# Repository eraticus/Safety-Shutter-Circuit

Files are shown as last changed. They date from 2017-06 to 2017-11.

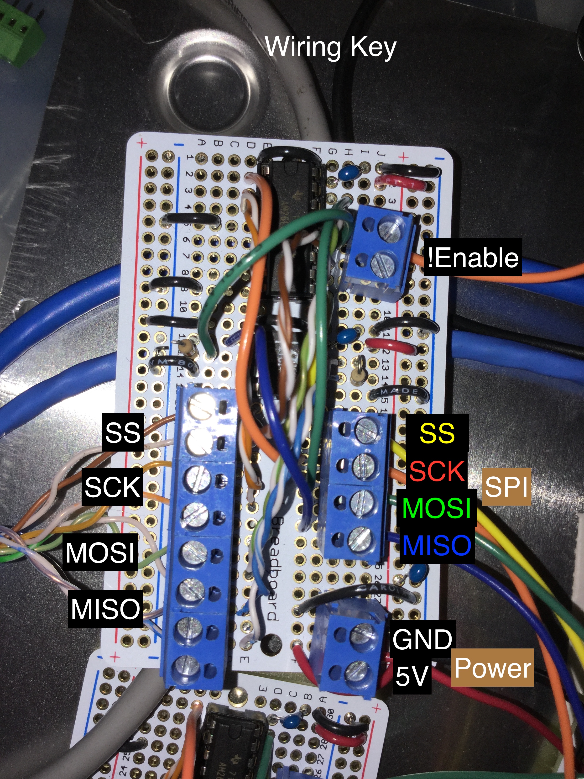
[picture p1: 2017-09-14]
images/IMG_2744.JPG

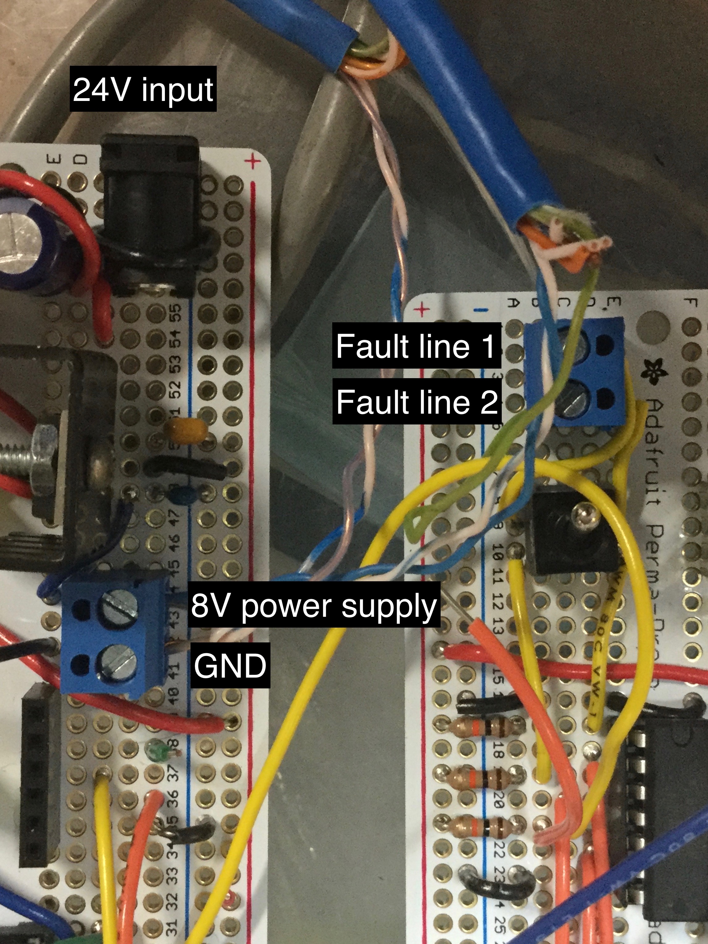
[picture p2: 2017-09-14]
images/IMG_2812.jpg

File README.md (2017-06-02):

# Safety-Shutter-Circuit
Circuit to close shutter if light levels get too high.
The project is separated into three components:
a) Sensors: photodiode amplifier circuit with comparator. Comparator goes low if light too high.
b) ADC: Can be connected with up to four sensor boards. ADC converts light level to digital value. Communication with Shutter Control board via SPI over differential pairs. Also, sensor comparator values ANDed. If a sensors comparator goes low, then a separate low signal sent to shutter control.
c) Shutter Control: Shutter control has multiple subsystems
  1) If a low signal is received from the ADC, a latch is set which controls the state of the shutter.
  2) The light levels are monitored, via the ADC boards, and if the light level approaches the threshold, the shutter is closed.
  3) Communication to LANTRONIX via RS-232 driver connected to RX/TX of microcontroller.

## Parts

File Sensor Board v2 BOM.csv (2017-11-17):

Digi-Key Part Number | Manufacturer | Manufacturer Part Number | Customer Reference | Quantity 1 | Quantity 2 | Quantity 3 | Mfg Std Lead Time | Description | Comments | RoHS Status | Lead Free Status | REACH Status
36-5015CT-ND | KEYSTONE ELECTRONICS (VA) | 5015 | TEST POINTS FOR FIELD CALIBRATION | 5 | 0 | 0 | 4 Weeks | PC TEST POINT MINIATURE SMT |  | RoHS Compliant | Lead free | Unaffected Jan-2017
399-1284-1-ND | KEMET (VA) | C0805C105K4RACTU | DECOUPLING CAPS FOR REGULATOR, ETC | 5 | 0 | 0 | 23 Weeks | CAP CER 1UF 16V X7R 0805 |  | RoHS Compliant | Lead free | Unaffected Jan-2017
3224G-1-103ECT-ND | BOURNS INC (VA) | 3224G-1-103E | FOR SETTING THRESHOLD VALUE | 1 | 0 | 0 | 8 Weeks | TRIMMER 10K OHM 0.25W SMD |  | RoHS Compliant | Lead free | Unaffected Jan-2017
160-1032-ND | LITE-ON INC | LTR-516AD | PHOTODIODE WITH DAYLIGHT FILTER | 1 | 0 | 0 | 14 Weeks | PHOTODIODE IR DARK |  | RoHS Compliant | Lead free | Not Available
MCP6541T-E/OTCT-ND | MICROCHIP TECHNOLOGY (VA) | MCP6541T-E/OT | SETS FAULT LINE BY COMPARING SENSOR TO THRESHOLD | 1 | 0 | 0 | 8 Weeks | IC COMP 1.6V SNGL P-P SOT23-5 |  | RoHS Compliant | Lead free | Unaffected Jan-2017
MCP6001T-E/OTCT-ND | MICROCHIP TECHNOLOGY (VA) | MCP6001T-E/OT | CHANGE PHOTOCURRENT TO VOLTAGE SIGNAL | 1 | 0 | 0 | 4 Weeks | IC OPAMP GP 1MHZ RRO SOT23-5 |  | RoHS Compliant | Lead free | Unaffected Jan-2017
MCP1702T-5002E/CBCT-ND | MICROCHIP TECHNOLOGY (VA) | MCP1702T-5002E/CB | 5 VOLT REG. USED TO POWER BOARD | 1 | 0 | 0 | 5 Weeks | IC REG LINEAR 5V 250MA SOT23A-3 |  | RoHS Compliant | Lead free | Unaffected Jan-2017
ED10564-ND | ON SHORE TECHNOLOGY INC | OSTVN05A150 | POWER INPUT SIGNAL OUTPUT | 1 | 0 | 0 | 10 Weeks | CONN TERM BLOCK 2.54MM 5POS PCB |  | RoHS Compliant | Lead free | Unaffected Jul-2017
399-1113-1-ND | KEMET (VA) | C0805C220J5GACTU | FEEDBACK STABILIZATION CAP | 1 | 0 | 0 | 18 Weeks | CAP CER 22PF 50V C0G/NP0 0805 |  | RoHS Compliant | Lead free | Unaffected Jan-2017
399-7442-1-ND | KEMET (VA) | C1206C106K3RACTU | UNREGULATED POWER INPUT CAP | 1 | 0 | 0 | 27 Weeks | CAP CER 10UF 25V X7R 1206 |  | RoHS Compliant | Lead free | Unaffected Jan-2017
YAG1242CT-ND | YAGEO (VA) | RT1206FRE0710KL | FEEDBACK RESISTOR | 1 | 0 | 0 | 20 Weeks | RES SMD 10K OHM 1% 1/4W 1206 | Alternate Packaging Exists | RoHS Compliant | Lead free | Unaffected Jul-2017

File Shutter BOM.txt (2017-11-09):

Partlist exported from /Users/eraticus/Library/Mobile Documents/com~apple~CloudDocs/Safety-Shutter-Circuit/Shutter.sch at 11/8/17 4:27 PM

Part                     Value                     Device                             Package                 Description                                   MF MPN         OC_FARNELL OC_NEWARK PROD_ID   
ADC1                     M08                       M08                                OSTVN08                                                                                                             
ADC1_FAULT               M03                       M03                                OSTVN03                                                                                                             
ADC2                     M08                       M08                                OSTVN08                                                                                                             
ADC2_FAULT               M03                       M03                                OSTVN03                                                                                                             
BUFFER_OD1:04CAP         100n                      CAP805B                            0805_B                                                                                                              
BUFFER_OD1:IC6           74AC04D                   74AC04D                            SO14                    Hex INVERTER                                                                                
BUFFER_OD1:IC7           74ALS05D                  74ALS05D                           SO14                    Hex INVERTER, open collector                                                                
BUFFER_OD1:O5CAP         100n                      CAP805B                            0805_B                                                                                                              
C1                       1u                        CAP5MM                             CAP_CER_TDK_FK28_5MM    Ceramic Capacitor                                                                           
C2                       1u                        CAP5MM                             CAP_CER_TDK_FK28_5MM    Ceramic Capacitor                                                                           
C3                       1u                        CAP5MM                             CAP_CER_TDK_FK28_5MM    Ceramic Capacitor                                                                           
C4                       1u                        CAP5MM                             CAP_CER_TDK_FK28_5MM    Ceramic Capacitor                                                                           
C5                       100n                      CAP805B                            0805_B                                                                                                              
C6                       100n                      CAP805B                            0805_B                                                                                                              
C7                       100n                      CAP805B                            0805_B                                                                                                              
C8                       100n                      CAP805B                            0805_B                                                                                                              
C9                       100n                      CAP805B                            0805_B                                                                                                              
C10                      100n                      CAP805B                            0805_B                                                                                                              
C11                      100n                      CAP805B                            0805_B                                                                                                              
C12                      100n                      CAP805B                            0805_B                                                                                                              
C13                      100n                      CAP805B                            0805_B                                                                                                              
C14                      100n                      CAP805B                            0805_B                                                                                                              
C15                      100n                      CAP805B                            0805_B                                                                                                              
C16                      1u                        CAP5MM                             CAP_CER_TDK_FK28_5MM    Ceramic Capacitor                                                                           
C17                      10u                       CAP_POL8_3.5                       CAP_POL_8_3.5           Polarized Capacitor, such as Electrolytic                                                   
C18                      1u                        CAP5MM                             CAP_CER_TDK_FK28_5MM    Ceramic Capacitor                                                                           
C19                      100n                      CAP805B                            0805_B                                                                                                              
CO[                      100n                      CAP805B                            0805_B                                                                                                              
D1                       AM26C31                   AM26C31                            SOIC_16_NARROW          Quadruple Differential Line Driver                                                          
D2                       AM26C31                   AM26C31                            SOIC_16_NARROW          Quadruple Differential Line Driver                                                          
D3                       1N4004                    1N4004                             DO41-10                 DIODE                                                                                       
DEWAR_SWITCH             M02                       M02                                OSTVN02                                                                                                             
IC3                      MAX3222                   MAX3222                            DIL18                   RS232 TRANSCEIVER                                MAX3222EPN+ 1188044    99K3237             
IC4                      74AC00D                   74AC00D                            SO14                    Quad 2-input NAND gate                                                                      
J1                       ATMEL_PROGRAMMER_HEADERTH ATMEL_PROGRAMMER_HEADERTH          ATMEL_PROGRAMMER_HEADER Board connector for Atmel MkII ISP programmer                                               
J2                                                 M06NO_SILK_FEMALE_PTH              1X06_NO_SILK            Header 6                                                                          CONN-08437
MC7808                   7808T                     7808T                              TO220H                  Positive VOLTAGE REGULATOR                                                                  
MC7812                   7812TV                    7812TV                             TO220V                  Positive VOLTAGE REGULATOR                                                                  
OPEN_CLOSE_TOGGLE        M03                       M03                                OSTVN03                                                                                                             
POWER                    M02                       M02                                OSTVN02                                                                                                             
R1                       10K                       RESISTOR0805                       0805                                                                                                                
R2                       100                       RESISTOR0805                       0805                                                                                                                
R3                       100                       RESISTOR0805                       0805                                                                                                                
R4                       10K                       RESISTOR0805                       0805                                                                                                                
R5                       10K                       RESISTOR0805                       0805                                                                                                                
R6                       10K                       RESISTOR0805                       0805                                                                                                                
R7                       10K                       RESISTOR0805                       0805                                                                                                                
R8                       1.6K                      RESISTOR0805                       0805                                                                                                                
SHUTTER                  M02                       M02                                OSTVN02                                                                                                             
SHUTTER_CLOSED_INDICATOR M02                       M02                                OSTVN02                                                                                                             
SHUTTER_OPEN_INDICATOR   M02                       M02                                OSTVN02                                                                                                             
SHUTTER_SWITCH           M02                       M02                                OSTVN02                                                                                                             
T1                       TIP131                    TIP131                             TO220                   NPN BIPOLAR DARLINGTON TRANSISTOR                                                           
U$1                      ATMEGA_32828PDIP          ATMEGA_32828PDIP                   DIP-28                                                                                                              
U$2                      RESONATOR                 RESONATOR                          CSTCE                                                                                                               
U$3                      TACTILE                   TACTILE                            CB315FP                                                                                                             
U$4                      MO3                       MO3                                OSTVN03                                                                                                             
U$5                      LTC1485DIP                LTC1485DIP                         DIP-8                                                                                                               
U$6                      LTC1485DIP                LTC1485DIP                         DIP-8                                                                                                               
U$7                      DPDTA_DP                  DPDTA_DP                           A_DP_STRAIGHT_BRACKET                                                                                               
U1                                                 VOLTAGE_REGULATOR_LDOMCP1702_TO-92 TO-92                   MCP1702 3 terminal LDO                                                                      
V1                       POWER_JACK                POWER_JACK                         PJ-102AH                Standard Power Jack with Switch

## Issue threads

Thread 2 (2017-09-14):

### ISSUE TITLE
Create and test chopper amp noninverting circuit

### ISSUE THREAD

**Issue by meyerjohn** [eraticus/Safety-Shutter-Circuit#2]
Verify that basic noninverting op amp circuit will give zero (or near zero) output for V(inverting) == V(noninverting) == GND. Test this for high gains or high resistor values.

This is to test idea for suitability for second stage voltage amplifier circuit, if voltages from transimpedance stage are not high enough for ADC

**Comment by eraticus** [comment]
This might be a good idea to test. However, since we are not using a far IR diode, I'm going to close this for now. It would be a good idea to test a chopper amp within the current circuit architecture.

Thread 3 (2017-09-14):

### ISSUE TITLE
Find appropriate ADC with interrupt pin

### ISSUE THREAD

**Issue by meyerjohn** [eraticus/Safety-Shutter-Circuit#3]
It would be convenient to shutdown the microcontroller and communications while an ADC event is occurring so that switching noise does not affect the process.

The idea here is to initiate the ADC process, then sleep the controller. The controller when wakes when the ADC is finished and indicated by an interrupt pin. The controller can then read and communicate the values.

I believe that MAXIM has ADCs that operate at 5V, and have interrupt pins to indicate that a conversion is ready to read in.

**Comment by eraticus** [comment]
I did not find an ADC with an interrupt. So I designed the circuit with the MCP3008 10bit ADC.

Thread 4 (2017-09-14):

### ISSUE TITLE
Find values for photodiode

### ISSUE THREAD

**Issue by meyerjohn** [eraticus/Safety-Shutter-Circuit#4]
When Jaren did his Akamai project, he had expected current values that I would like to use in calculating op amp circuit gains. I also need to know what the capacitance of the photodiode is, in order to calculate stability, and capacitor compensation values.

This should be in my old notebook. If not, contact Jaren and Andre.

**Comment by eraticus** [comment]
Not using the far IR photodiodes. I use commercial 940nm photodiodes instead, since they will be mounted outside the dewar

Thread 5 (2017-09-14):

### ISSUE TITLE
Design NAND SR-Latch with avoidance of forbiden 00 state

### ISSUE THREAD

**Issue by meyerjohn** [eraticus/Safety-Shutter-Circuit#5]
I want to avoid both inputs going low, which would occur if there was an attempt to reset the latch when the circuit is currently faulting.

I have an idea of gating the input to S via an AND gate. By tying input A of the AND to R, the value of AND becomes a buffer for the B input. Attaching Y of AND to a 74HC05 makes it a NAND with OC output.

A 74HC03 chip is not a normally stocked part, but it is available.

**Comment by eraticus** [comment]
I'm closing this without rewiring the circuit for LOW/LOW input avoidance. This is because I don't anticipate this to be a problem. The interface via micro controller can check the state of the photodiodes first (via the fault lines).

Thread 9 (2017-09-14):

### ISSUE TITLE
Install MCP3008 10 bit ADC

### ISSUE THREAD

**Issue by meyerjohn** [eraticus/Safety-Shutter-Circuit#9]
Maybe don't write separate library, but have all code that interfaces with MCP3008 in a separate file.
[datasheet](http://ww1.microchip.com/downloads/en/DeviceDoc/21295d.pdf)

**Comment by eraticus** [comment]
The code for the MCP3008 is complete. There are some "improvements" that could be done, such as separating into a lib, and left justifying the data, and only using 8bits. I will wait for someone to ask me for this though. It works now.

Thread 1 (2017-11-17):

### ISSUE TITLE
Documentation: Create spreadsheet for stability and gain calculations for candidate op amps

### ISSUE THREAD

**Issue by meyerjohn** [eraticus/Safety-Shutter-Circuit#1]
Need this to determine applicability of a particular op amp, and maximum gain. Maximum gain might be limited by maximum resistor value is available.

**Comment by eraticus** [comment]
I did these calculations earlier for the feedback capacitor on the transconductive op amp circuits for the photodiode. Not sure if I need to preserve, but find the white paper that the work was based on for reference. I think it was a Microchip white paper

**Comment by eraticus** [comment]
Since the gain resistor has been reduced to 10K, this is no longer really necessary.

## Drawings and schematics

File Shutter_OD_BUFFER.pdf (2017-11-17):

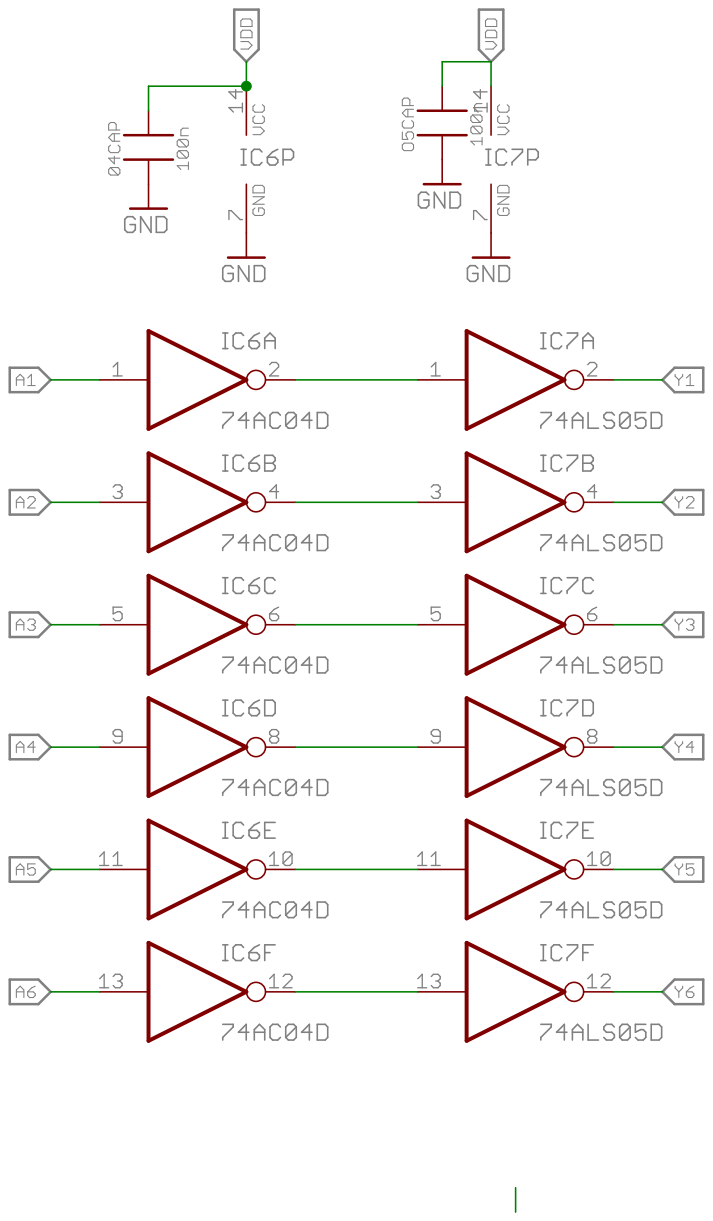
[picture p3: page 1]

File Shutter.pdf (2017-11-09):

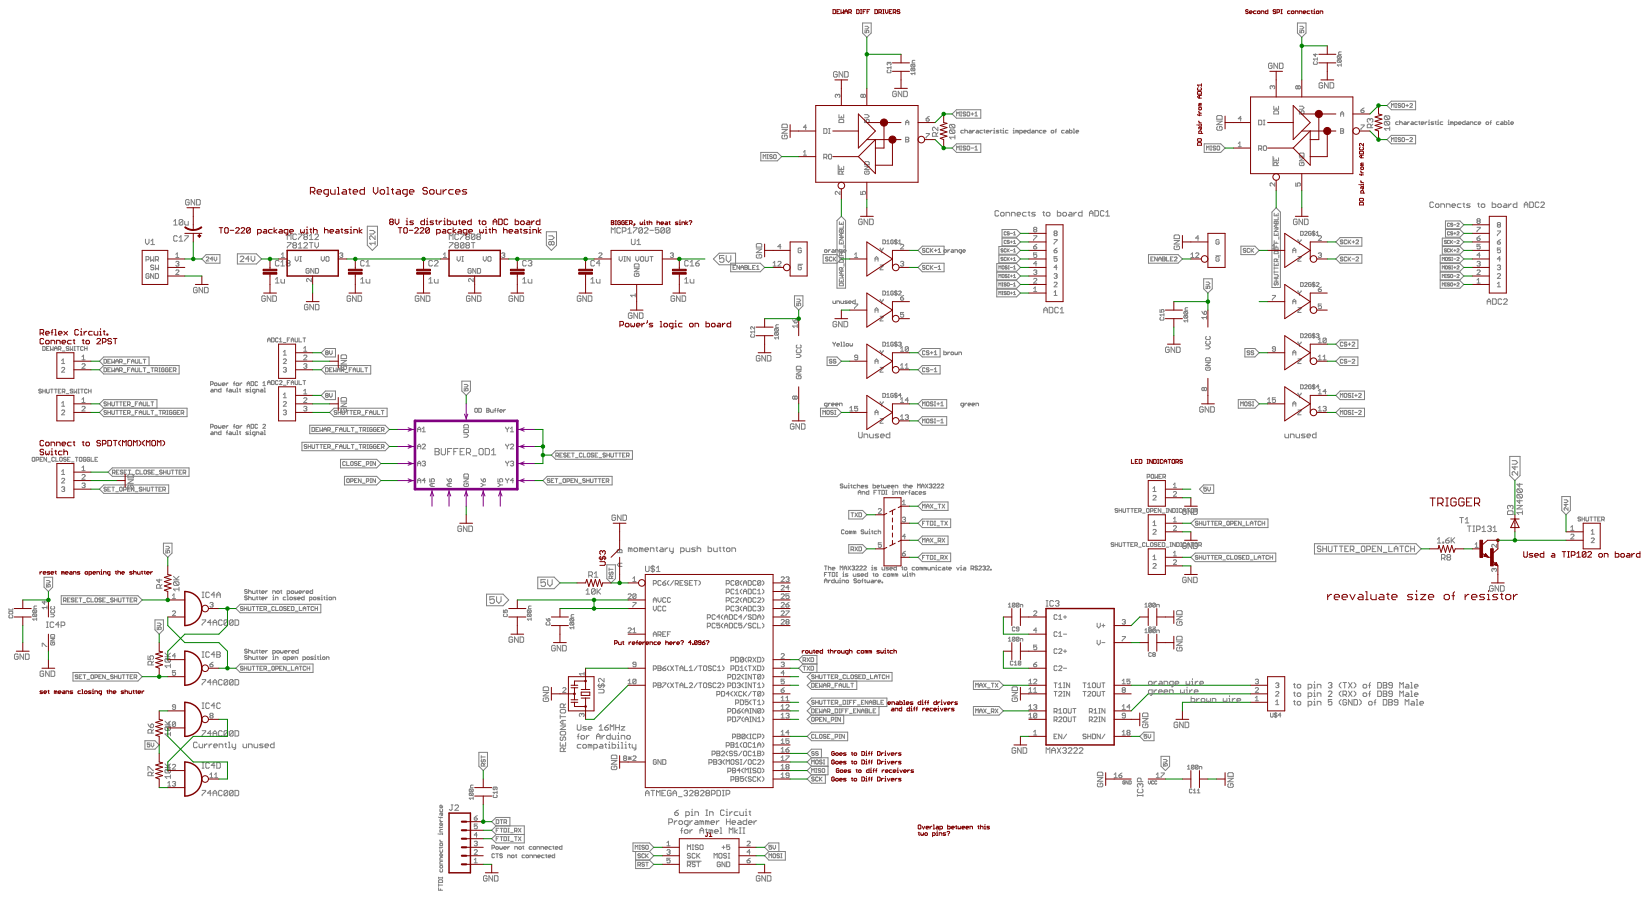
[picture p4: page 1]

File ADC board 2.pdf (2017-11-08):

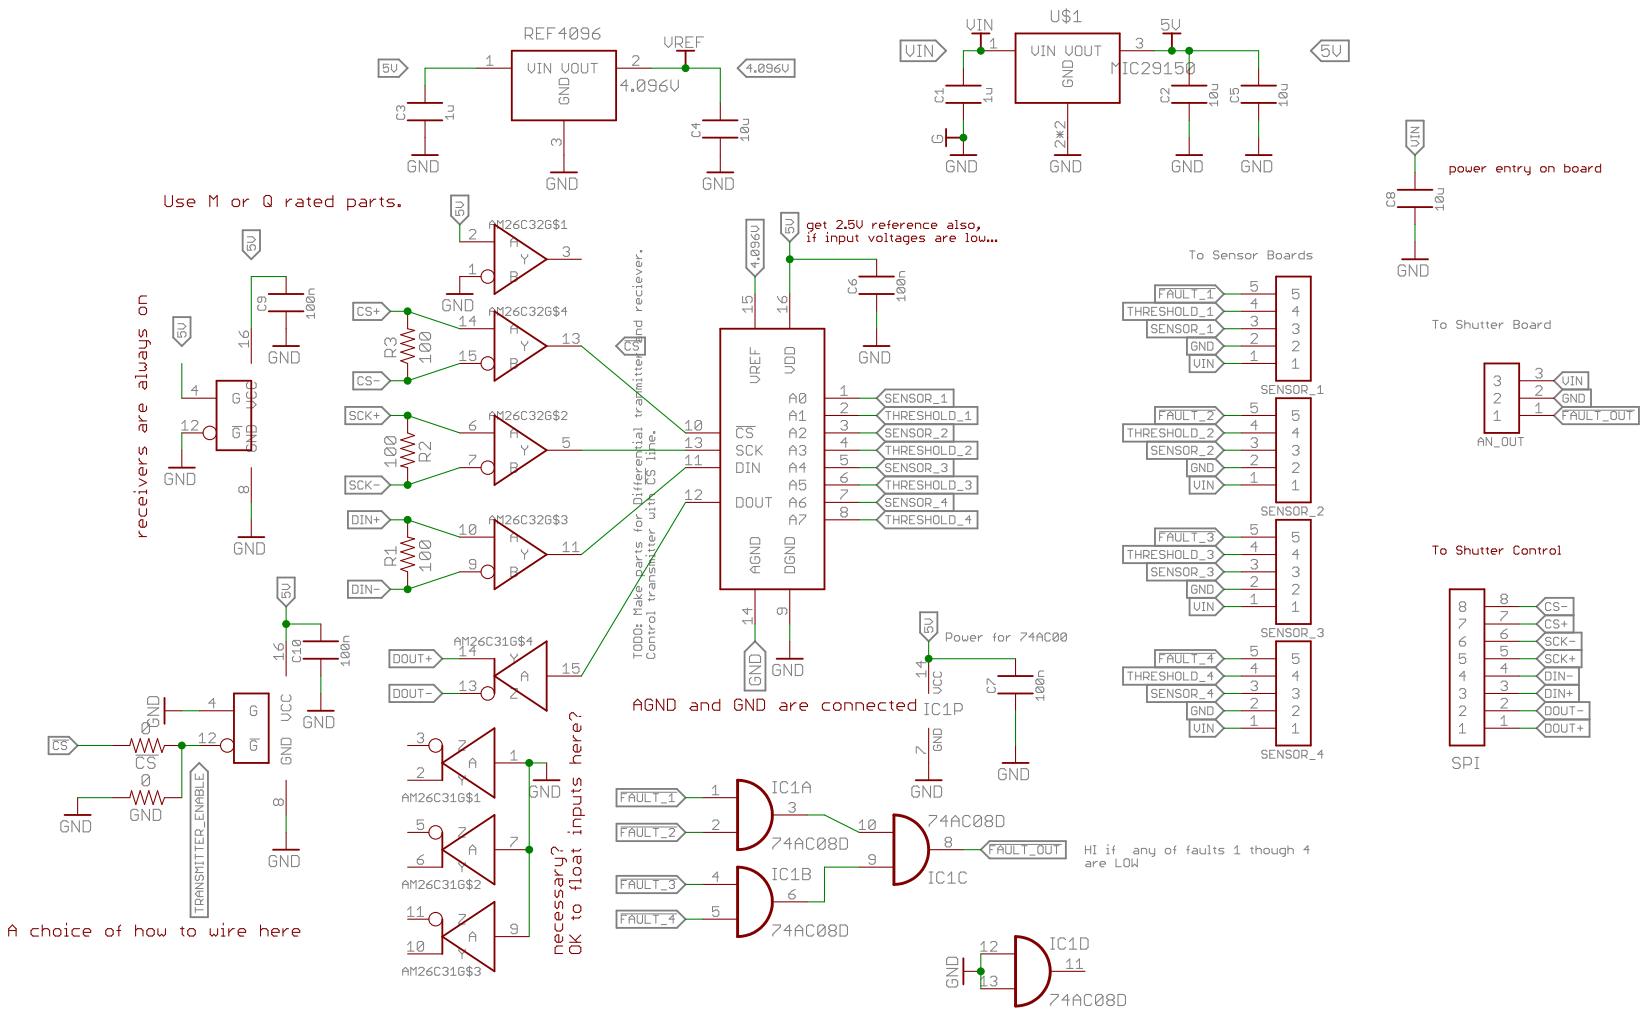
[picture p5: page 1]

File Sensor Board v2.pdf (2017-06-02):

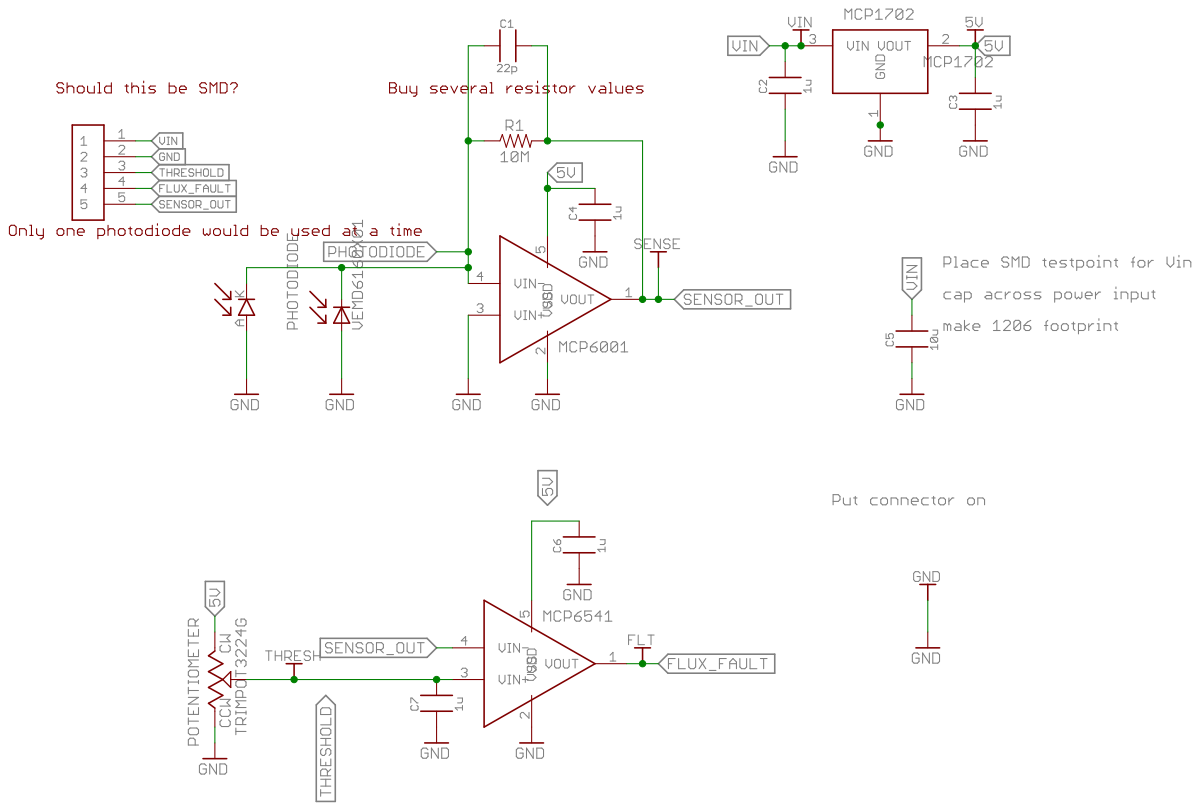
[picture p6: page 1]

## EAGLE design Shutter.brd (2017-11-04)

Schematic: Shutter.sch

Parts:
ADC1, ADC2: M08; OSTVN08
ADC1_FAULT, ADC2_FAULT: M03; OSTVN03
C1, C2, C3, C4, C16, C18: 1u; CAP_CER_TDK_FK28_5MM
C5, C6, C7, C8, C9, C10, C11, C12, C13, C14, C15, C19: 100n; 0805_B
C17: 10u; CAP_POL_8_3.5
CO[: 100n; 0805_B
D1, D2: AM26C31; SOIC_16_NARROW
D3: 1N4004; DO41-10
DEWAR_SWITCH: M02; OSTVN02
IC3: MAX3222; DIL18
IC4: 74AC00D; SO14
J1: ATMEL_PROGRAMMER_HEADERTH; ATMEL_PROGRAMMER_HEADER
J2: M06NO_SILK_FEMALE_PTH; 1X06_NO_SILK
MC7808: 7808T; TO220H
MC7812: 7812TV; TO220V
OPEN_CLOSE_TOGGLE: M03; OSTVN03
POWER: M02; OSTVN02
R1, R4, R5, R6, R7: 10K; 0805
R2, R3: 100; 0805
R8: 1.6K; 0805
SHUTTER: M02; OSTVN02
SHUTTER_CLOSED_INDICATOR: M02; OSTVN02
SHUTTER_OPEN_INDICATOR: M02; OSTVN02
SHUTTER_SWITCH: M02; OSTVN02
T1: TIP131; TO220
U1: VOLTAGE_REGULATOR_LDOMCP1702_TO-92; TO-92
U$1: ATMEGA_32828PDIP; DIP-28
U$2: RESONATOR; CSTCE
U$3: TACTILE; CB315FP
U$4: MO3; OSTVN03
U$5, U$6: LTC1485DIP; DIP-8
U$7: DPDTA_DP; A_DP_STRAIGHT_BRACKET
V1: POWER_JACK; PJ-102AH

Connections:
5V: C5.2, C6.2, C11.2, C12.2, C13.2, C14.2, C15.2, C16.P$1 (1), CO[.2, D1.16 (VCC), D2.16 (VCC), IC3.17 (VCC), IC3.18 (SHDN/), IC4.14 (VCC), J1.2 (+5), POWER.1, R1.1, R4.2, R5.2, R6.1, R7.2, U1.3 (VOUT), U$1.7 (VCC), U$1.20 (AVCC), U$5.8 (5V), U$6.8 (5V); also elsewhere on the board
8V: ADC1_FAULT.1, ADC2_FAULT.1, C3.P$1 (1), C4.P$1 (1), MC7808.3 (VO), U1.2 (VIN)
12V: C1.P$1 (1), C2.P$1 (1), MC7808.1 (VI), MC7812.3 (VO)
24V: C17.+, C18.P$1 (1), D3.C, MC7812.1 (VI), SHUTTER.1, V1.1 (PWR)
CLOSE_PIN: U$1.14 (PB0(ICP)); also elsewhere on the board
CS+1: ADC1.7, D1.10 (Y)
CS+2: ADC2.7, D2.10 (Y)
CS-1: ADC1.8, D1.11 (Z)
CS-2: ADC2.8, D2.11 (Z)
DEWAR_DIFF_ENABLE: U$1.12 (PD6(AIN0)), U$5.2 (!RE!)
DEWAR_FAULT: ADC1_FAULT.3, DEWAR_SWITCH.1, U$1.5 (PD3(INT1))
DEWAR_FAULT_TRIGGER: DEWAR_SWITCH.2; also elsewhere on the board
DTR: C19.2, J2.6
ENABLE1: D1.12 (!G!)
ENABLE2: D2.12 (!G!)
FTDI_RX: J2.5, U$7.6 (U1)
FTDI_TX: J2.4, U$7.3 (U)
GND: ADC1_FAULT.2, ADC2_FAULT.2, C1.P$2 (2), C2.P$2 (2), C3.P$2 (2), C4.P$2 (2), C5.1, C6.1, C7.1, C8.1, C11.1, C12.1, C13.1, C14.1, C15.1, C16.P$2 (2), C17.-, C18.P$2 (2), CO[.1, D1.4 (G), D1.7 (A), D1.8 (GND), D2.4 (G), D2.8 (GND), IC3.1 (EN/), IC3.9 (R2IN), IC3.11 (T2IN), IC3.16 (GND), IC4.7 (GND), J1.6 (GND), J2.1, MC7808.2 (GND), MC7812.2 (GND), OPEN_CLOSE_TOGGLE.2, POWER.2, SHUTTER_CLOSED_INDICATOR.2, SHUTTER_OPEN_INDICATOR.2, T1.3 (E), U1.1 (GND), U$1.8 (GND), U$1.22 (GND), U$2.2, U$3.3 (B), U$3.4 (B), U$4.1, U$5.3 (DE), U$5.4 (DI), U$5.5 (GND), U$6.3 (DE), U$6.4 (DI), U$6.5 (GND), V1.2 (GND); also elsewhere on the board
MAX_RX: IC3.13 (R1OUT), U$7.4 (D1)
MAX_TX: IC3.12 (T1IN), U$7.1 (D)
MISO: J1.1 (MISO), U$1.18 (PB4(MISO)), U$5.1 (RO), U$6.1 (RO)
MISO+1: ADC1.1, R2.2, U$5.6 (A)
MISO+2: ADC2.1, R3.2, U$6.6 (A)
MISO-1: ADC1.2, R2.1, U$5.7 (B)
MISO-2: ADC2.2, R3.1, U$6.7 (B)
MOSI: D1.15 (A), D2.15 (A), J1.4 (MOSI), U$1.17 (PB3(MOSI/OC2))
MOSI+1: ADC1.3, D1.14 (Y)
MOSI+2: ADC2.3, D2.14 (Y)
MOSI-1: ADC1.4, D1.13 (Z)
MOSI-2: ADC2.4, D2.13 (Z)
unnamed: U$1.9 (PB6(XTAL1/TOSC1)), U$2.1
unnamed: U$1.10 (PB7(XTAL2/TOSC2)), U$2.3
unnamed: C7.2, IC3.3 (V+)
unnamed: C8.2, IC3.7 (V-)
unnamed: C9.1, IC3.2 (C1+)
unnamed: C10.1, IC3.5 (C2+)
unnamed: C9.2, IC3.4 (C1-)
unnamed: C10.2, IC3.6 (C2-)
unnamed: D3.A, SHUTTER.2, T1.2 (C)
unnamed: IC4.9 (I0), R6.2
unnamed: IC4.13 (I1), R7.1
unnamed: IC4.10 (I1), IC4.11 (O)
unnamed: IC4.8 (O), IC4.12 (I0)
unnamed: R8.1, T1.1 (B)
OPEN_PIN: U$1.13 (PD7(AIN1)); also elsewhere on the board
RESET_CLOSE_SHUTTER: IC4.1 (I0), OPEN_CLOSE_TOGGLE.1, R4.1; also elsewhere on the board
RST: C19.1, J1.5 (!RST!), R1.2, U$1.1 (PC6(/RESET)), U$3.1 (A), U$3.2 (A)
RX: IC3.14 (R1IN), U$4.2
RXD: U$1.2 (PD0(RXD)), U$7.5 (C1)
SCK: D1.1 (A), D2.1 (A), J1.3 (SCK), U$1.19 (PB5(SCK))
SCK+1: ADC1.5, D1.2 (Y)
SCK+2: ADC2.5, D2.2 (Y)
SCK-1: ADC1.6, D1.3 (Z)
SCK-2: ADC2.6, D2.3 (Z)
SET_OPEN_SHUTTER: IC4.5 (I1), OPEN_CLOSE_TOGGLE.3, R5.1; also elsewhere on the board
SHUTTER_CLOSED_LATCH: IC4.3 (O), IC4.4 (I0), SHUTTER_CLOSED_INDICATOR.1, U$1.4 (PD2(INT0))
SHUTTER_DIFF_ENABLE: U$1.11 (PD5(T1)), U$6.2 (!RE!)
SHUTTER_FAULT: ADC2_FAULT.3, SHUTTER_SWITCH.1
SHUTTER_FAULT_TRIGGER: SHUTTER_SWITCH.2; also elsewhere on the board
SHUTTER_OPEN_LATCH: IC4.2 (I1), IC4.6 (O), R8.2, SHUTTER_OPEN_INDICATOR.1
SS: D1.9 (A), D2.9 (A), U$1.16 (PB2(SS/OC1B))
SW: V1.3 (SW)
TX: IC3.15 (T1OUT), U$4.3
TXD: U$1.3 (PD1(TXD)), U$7.2 (C)

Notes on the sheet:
Regulated Voltage Sources
Put reference here? 4.096?
routed through comm switch
Goes to diff receivers
Goes to Diff Drivers
enables diff drivers and diff receivers
DEWAR DIFF DRIVERS
Second SPI connection
DO pair from ADC1
DO pair from ADC2
OD Buffer
Shutter not powered Shutter in closed position
Shutter powered Shutter in open position
TO-220 package with heatsink
Power's logic on board
reset means opening the shutter
set means closing the shutter
8V is distributed to ADC board
Overlap between this two pins?
LED INDICATORS
BIGGER, with heat sink?
TRIGGER
reevaluate size of resistor
Used a TIP102 on board
Reflex Circuit. Connect to 2PST
Connect to SPDT(MOM)(MOM) Switch

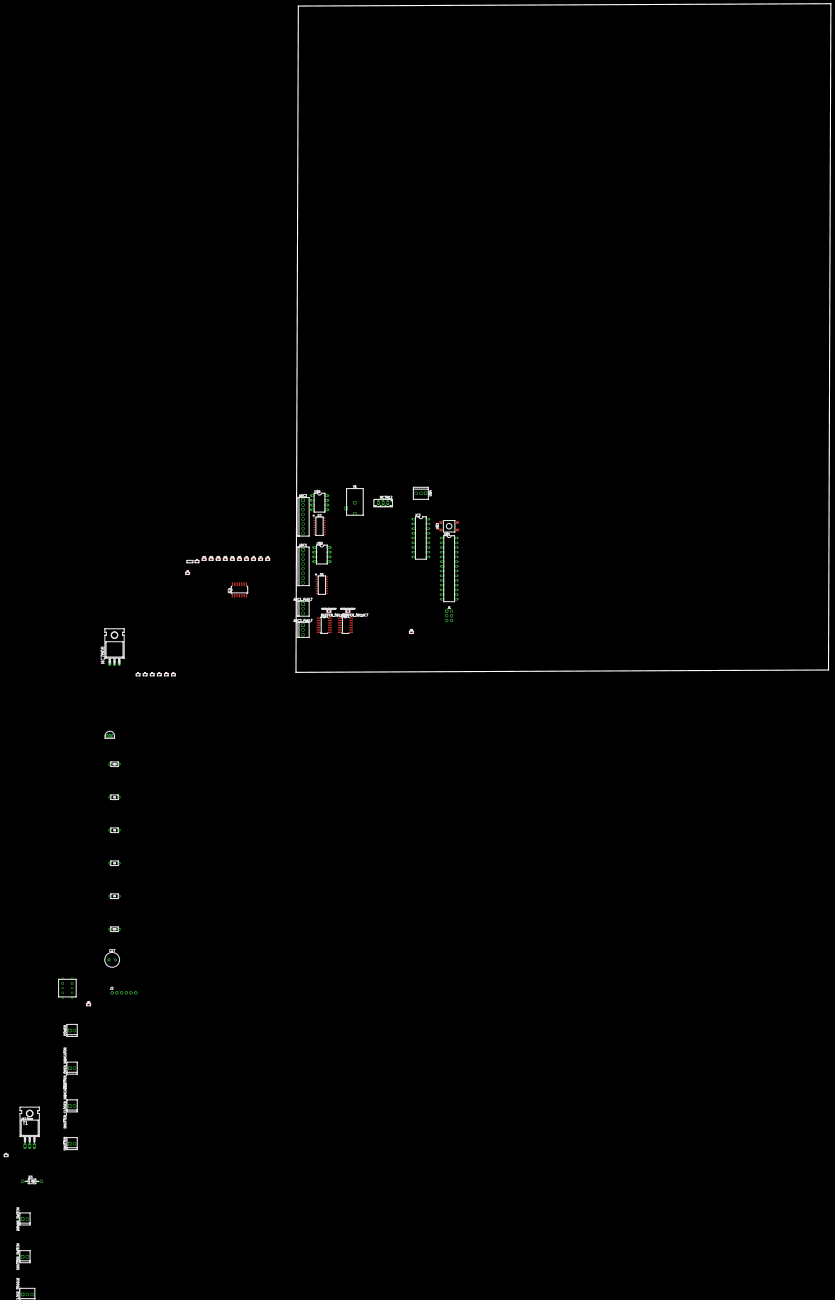
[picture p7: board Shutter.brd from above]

Board: 2 copper layers, 288.3 x 360.4 mm, 62 parts (0 on the bottom side), 67 nets, no tracks yet.

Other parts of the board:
BUFFER_OD1:04CAP, BUFFER_OD1:O5CAP: 100n; 0805_B
BUFFER_OD1:IC6: 74AC04D; SO14
BUFFER_OD1:IC7: 74ALS05D; SO14

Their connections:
5V: BUFFER_OD1:04CAP.2, BUFFER_OD1:IC6.14, BUFFER_OD1:IC7.14, BUFFER_OD1:O5CAP.2; also elsewhere on the board
BUFFER_OD1:N$1: BUFFER_OD1:IC6.2, BUFFER_OD1:IC7.1
BUFFER_OD1:N$2: BUFFER_OD1:IC6.10, BUFFER_OD1:IC7.11
BUFFER_OD1:N$3: BUFFER_OD1:IC6.12, BUFFER_OD1:IC7.13
BUFFER_OD1:N$36: BUFFER_OD1:IC6.4, BUFFER_OD1:IC7.3
BUFFER_OD1:N$37: BUFFER_OD1:IC6.6, BUFFER_OD1:IC7.5
BUFFER_OD1:N$38: BUFFER_OD1:IC6.8, BUFFER_OD1:IC7.9
CLOSE_PIN: BUFFER_OD1:IC6.5; also elsewhere on the board
DEWAR_FAULT_TRIGGER: BUFFER_OD1:IC6.1; also elsewhere on the board
GND: BUFFER_OD1:04CAP.1, BUFFER_OD1:IC6.7, BUFFER_OD1:IC7.7, BUFFER_OD1:O5CAP.1; also elsewhere on the board
OPEN_PIN: BUFFER_OD1:IC6.9; also elsewhere on the board
RESET_CLOSE_SHUTTER: BUFFER_OD1:IC7.2, BUFFER_OD1:IC7.4, BUFFER_OD1:IC7.6; also elsewhere on the board
SET_OPEN_SHUTTER: BUFFER_OD1:IC7.8; also elsewhere on the board
SHUTTER_FAULT_TRIGGER: BUFFER_OD1:IC6.3; also elsewhere on the board

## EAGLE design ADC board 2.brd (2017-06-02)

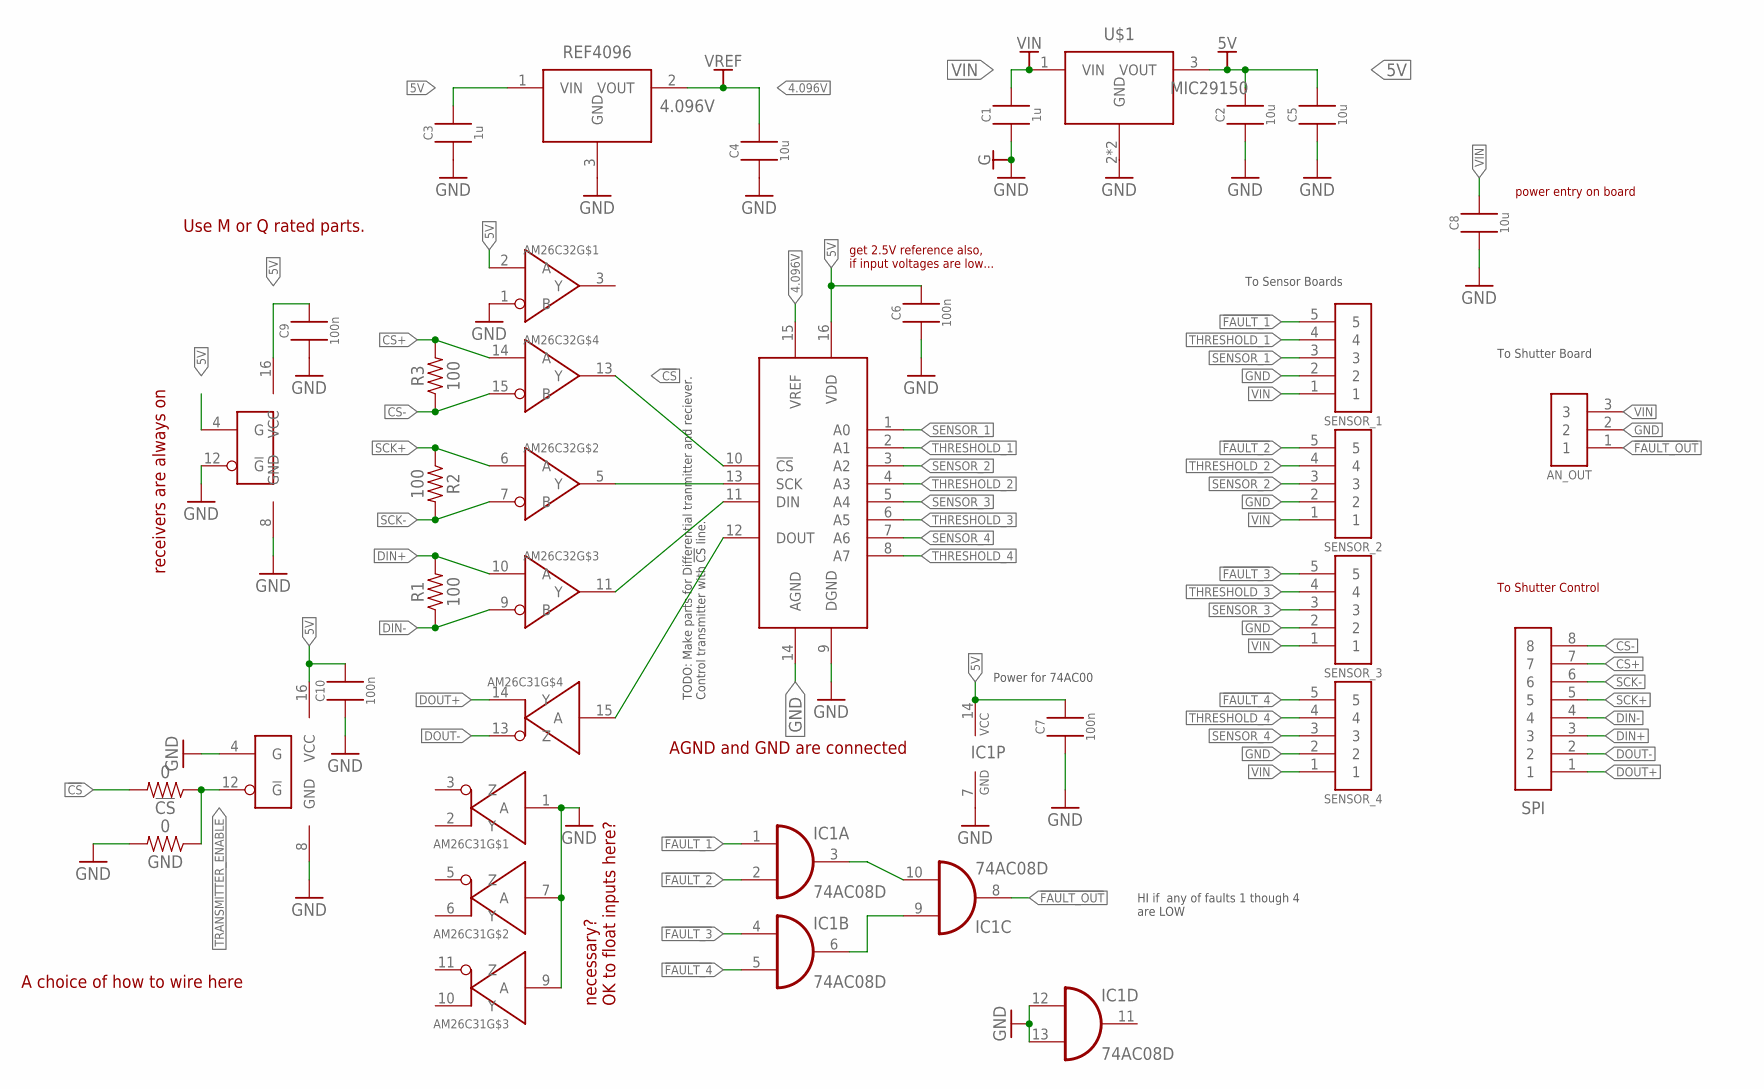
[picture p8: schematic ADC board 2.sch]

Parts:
5V: TEST_POINT5015; 5015
!CS!: 0; 1206
AM26C31: AM26C31; SOIC_16_NARROW
AM26C32: AM26C32; SOIC_16_NARROW
AN_OUT: MO3; OSTVN03
C1, C3: 1u; 0805_B
C2, C4, C5, C8: 10u; 1206_A
C6, C7, C9, C10: 100n; 0805_B
G: TEST_POINT5015; 5015
GND: 0; 1206
IC1: 74AC08D; SO14
MCP3008: MCP3008MCP3008; SOIC-16-NARROW
R1, R2, R3: 100; 1206
REF4096: 4.096V; SOT23A(CB)
SENSOR_1, SENSOR_2, SENSOR_3, SENSOR_4: M05OSTVN05; OSTVN05
SPI: M08; OSTVN08
U$1: MIC29150; TO263-3
VIN: TEST_POINT5015; 5015
VREF: TEST_POINT5015; 5015

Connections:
4.096V: C4.2, MCP3008.15 (VREF), REF4096.2 (VOUT), VREF.1
5V: 5V.1, AM26C31.16 (VCC), AM26C32.2 (A), AM26C32.4 (G), AM26C32.16 (VCC), C2.2, C3.2, C5.2, C6.2, C7.2, C9.2, C10.2, IC1.14 (VCC), MCP3008.16 (VDD), REF4096.1 (VIN), U$1.3 (VOUT)
!CS!: !CS!.2, AM26C32.13 (Y), MCP3008.10 (!CS!)
!FAULT_1: IC1.1 (I0), SENSOR_1.5
!FAULT_2: IC1.2 (I1), SENSOR_2.5
!FAULT_3: IC1.4 (I0), SENSOR_3.5
!FAULT_4: IC1.5 (I1), SENSOR_4.5
!FAULT_OUT!: AN_OUT.1, IC1.8 (O)
CS+: AM26C32.14 (A), R3.2, SPI.7
CS-: AM26C32.15 (B), R3.1, SPI.8
DIN: AM26C32.11 (Y), MCP3008.11 (DIN)
DIN+: AM26C32.10 (A), R1.2, SPI.3
DIN-: AM26C32.9 (B), R1.1, SPI.4
DOUT: AM26C31.15 (A), MCP3008.12 (DOUT)
DOUT+: AM26C31.14 (Y), SPI.1
DOUT-: AM26C31.13 (Z), SPI.2
GND: AM26C31.1 (A), AM26C31.4 (G), AM26C31.7 (A), AM26C31.8 (GND), AM26C31.9 (A), AM26C32.1 (B), AM26C32.8 (GND), AM26C32.12 (!G!), AN_OUT.2, C1.1, C2.1, C3.1, C4.1, C5.1, C6.1, C7.1, C8.1, C9.1, C10.1, G.1, GND.2, IC1.7 (GND), IC1.12 (I0), IC1.13 (I1), MCP3008.9 (DGND), MCP3008.14 (AGND), REF4096.3 (GND), SENSOR_1.2, SENSOR_2.2, SENSOR_3.2, SENSOR_4.2, U$1.2 (GND), U$1.P$3 (GND)
unnamed: IC1.3 (O), IC1.10 (I1)
unnamed: IC1.6 (O), IC1.9 (I0)
SCK: AM26C32.5 (Y), MCP3008.13 (SCK)
SCK+: AM26C32.6 (A), R2.1, SPI.5
SCK-: AM26C32.7 (B), R2.2, SPI.6
SENSOR_1: MCP3008.1 (A0), SENSOR_1.3
SENSOR_2: MCP3008.3 (A2), SENSOR_2.3
SENSOR_3: MCP3008.5 (A4), SENSOR_3.3
SENSOR_4: MCP3008.7 (A6), SENSOR_4.3
THRESHOLD_1: MCP3008.2 (A1), SENSOR_1.4
THRESHOLD_2: MCP3008.4 (A3), SENSOR_2.4
THRESHOLD_3: MCP3008.6 (A5), SENSOR_3.4
THRESHOLD_4: MCP3008.8 (A7), SENSOR_4.4
TRANSMITTER_ENABLE: !CS!.1, AM26C31.12 (!G!), GND.1
VIN: AN_OUT.3, C1.2, C8.2, SENSOR_1.1, SENSOR_2.1, SENSOR_3.1, SENSOR_4.1, U$1.1 (VIN), VIN.1

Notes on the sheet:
HI if any of faults 1 though 4 are LOW
Power for 74AC00
TODO: Make parts for Differential tranmitter and reciever. Control transmitter with !CS! line.
To Sensor Boards
To Shutter Board
power entry on board
To Shutter Control
A choice of how to wire here
receivers are always on
necessary? OK to float inputs here?
Use M or Q rated parts.
get 2.5V reference also, if input voltages are low...
AGND and GND are connected

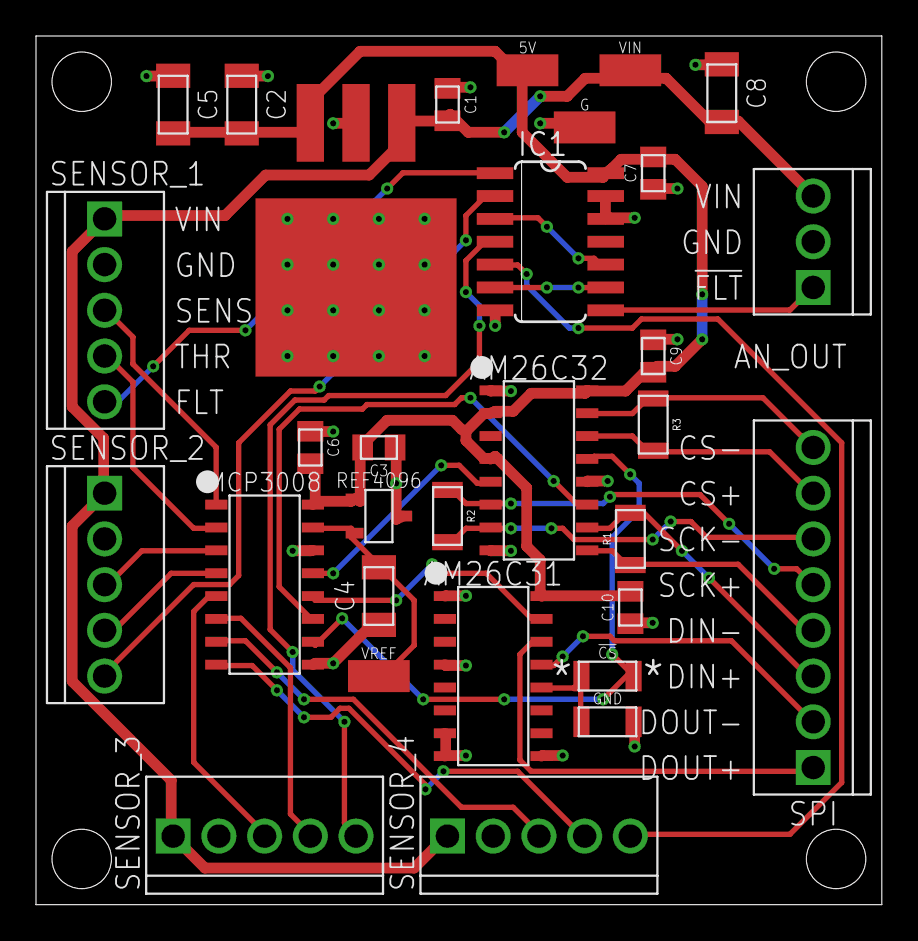
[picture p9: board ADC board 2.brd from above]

Board: 2 copper layers, 47.0 x 48.3 mm, 35 parts (0 on the bottom side), 32 nets.

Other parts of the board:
U$2, U$4, U$5, U$6: STAND-OFF

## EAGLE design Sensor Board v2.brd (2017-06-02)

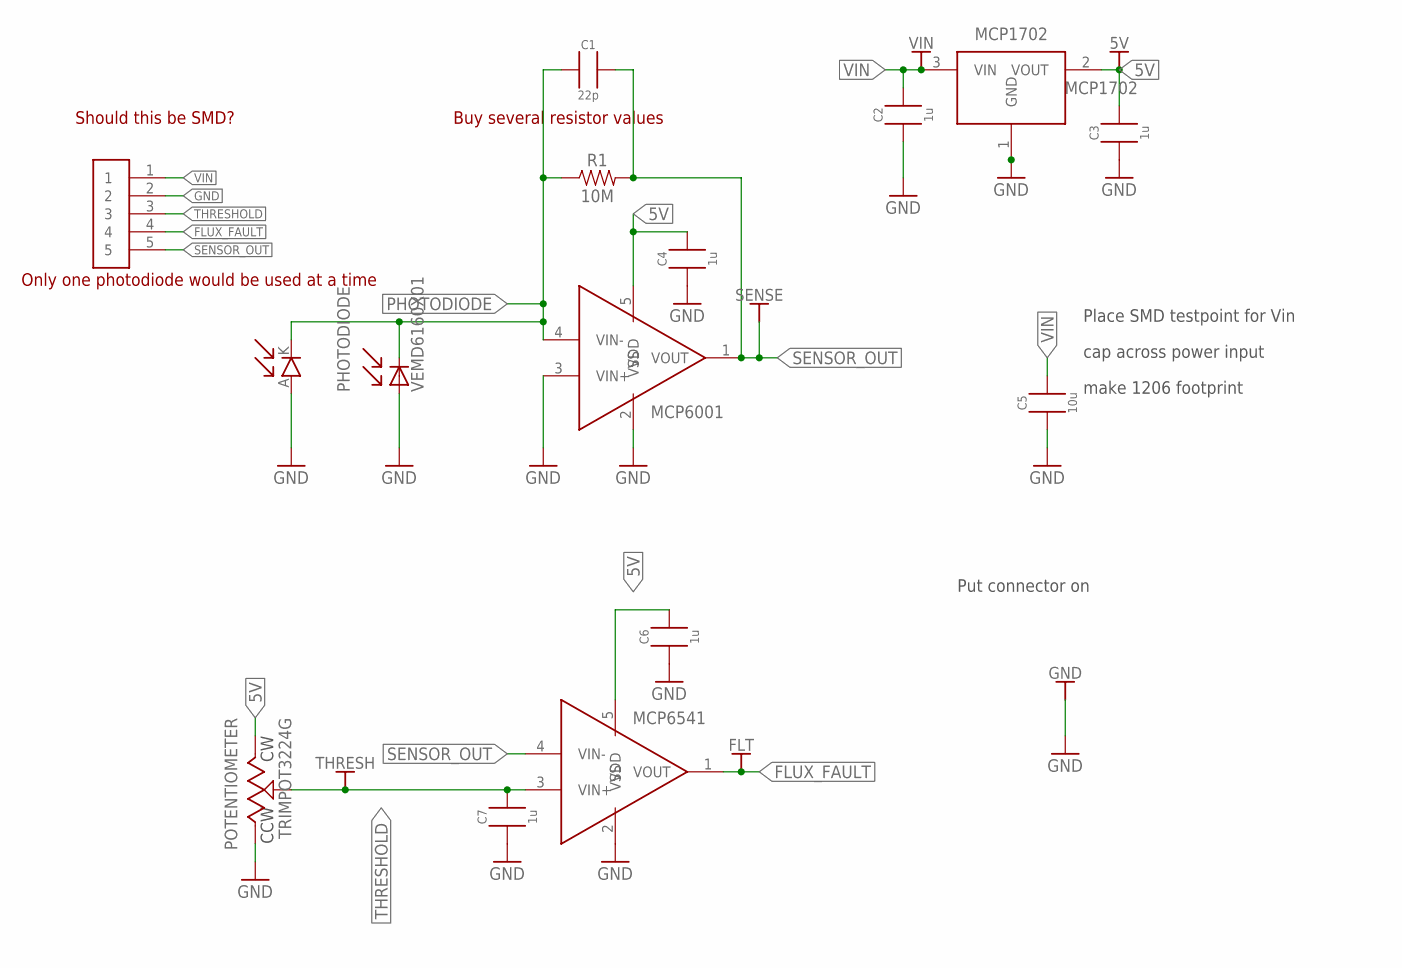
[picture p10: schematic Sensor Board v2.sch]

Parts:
5V: TEST_POINT5015; 5015
C1: 22p; 0805_C
C2: 1u; 0805_C
C3, C4, C6, C7: 1u; 0805_B
C5: 10u; 1206_A
FLT: TEST_POINT5015; 5015
GND: TEST_POINT5015; 5015
MCP1702: MCP1702; SOT23A(CB)
MCP6001: MCP6001MCP6001; SOT23(OT)
MCP6541: MCP6541; SOT23(OT)
PHOTODIODE: VEMD6160X01
R1: 10M; 1206
SENSE: TEST_POINT5015; 5015
THRESH: TEST_POINT5015; 5015
TRIMPOT3224G: POTENTIOMETER; 3224G
U$1: M05OSTVN05; OSTVN05
U$2: PHOTODIODE; LTR-516AD
VIN: TEST_POINT5015; 5015

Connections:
5V: 5V.1, C3.2, C4.2, C6.2, MCP1702.2 (VOUT), MCP6001.5 (VDD), MCP6541.5 (VDD), TRIMPOT3224G.3 (CW)
FLUX_FAULT: FLT.1, MCP6541.1 (VOUT), U$1.4
GND: C2.1, C3.1, C4.1, C5.1, C6.1, C7.1, GND.1, MCP1702.1 (GND), MCP6001.2 (VSS), MCP6001.3 (VIN+), MCP6541.2 (VSS), PHOTODIODE.A1 (A), TRIMPOT3224G.1 (CCW), U$1.2, U$2.A
PHOTODIODE: C1.1, MCP6001.4 (VIN-), PHOTODIODE.K (C), R1.1, U$2.K (C)
SENSOR_OUT: C1.2, MCP6001.1 (VOUT), MCP6541.4 (VIN-), R1.2, SENSE.1, U$1.5
THRESHOLD: C7.2, MCP6541.3 (VIN+), THRESH.1, TRIMPOT3224G.2 (WIPER), U$1.3
VIN: C2.2, C5.2, MCP1702.3 (VIN), U$1.1, VIN.1

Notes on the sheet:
Put connector on
cap across power input
make 1206 footprint
Place SMD testpoint for Vin
Only one photodiode would be used at a time
Buy several resistor values
Should this be SMD?

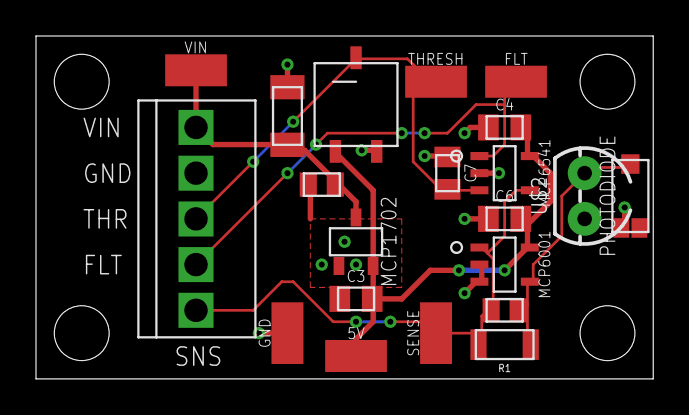
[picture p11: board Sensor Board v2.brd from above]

Board: 2 copper layers, 34.3 x 19.1 mm, 25 parts (0 on the bottom side), 7 nets.

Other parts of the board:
U$3, U$4, U$5, U$6: STAND-OFF-TIGHT

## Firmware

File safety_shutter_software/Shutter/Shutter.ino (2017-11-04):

// TODO LIST
// check add input lines to latch to "see" open/closed status physically, since can change assynchronously from a) toggle, and b) reflex circuit
// add input line to reflex input to "see"
// add "sensor" lines for status of shutter
// add "actuator lines for "close shutter" and "open shutter"
// add command to disable closing of shutter via software. This is needed for calibration.
// convert #DEFINE to const, or vice versa
// arrange const list into at least two categories:
// a) time constants; and
// b) pin constants

// adds a bunch of print statements to help with development

#include <SPI.h>

//#define DEBUG

/* are these used? Needed? */
#define CLOS "CLOSE"
#define OPEN "OPEN"
#define STAT "STATUS"

//ADC interval is 1/4 second
const unsigned long adc_interval = 1000; // two seconds. Nice and long for testing and debugging
//const unsigned long adc_interval = 5000;

const unsigned long enable_delay = 30;
const unsigned long cs_delay = 30;


const int ENABLE_DEWAR_ADC_PIN = 6;
const int ENABLE_SHUTTER_ADC_PIN = 5;

const int SENSOR_TRIGGERING_PIN = 3;

const int GET_SHUTTER_CLOSED_PIN = 2;
const int REFLEX_FAULT = 3; // put ISR on rising edge to set fault flag

//TODO: Wire these up
#define SHUTTER_OPEN_PIN 7
#define SHUTTER_CLOSE_PIN 8

// SPI chip select line
#define CS 10

int bufPos = 0;
char buf[256];

// raw data from first ADC
unsigned int adc_data_dewar[] = {
  0, 0, 0, 0, 0, 0, 0, 0
};

// raw data from second ADC
unsigned int adc_data_shutter[] = {
  0, 0, 0, 0, 0, 0, 0, 0
};


volatile boolean fault_flag = false;

/*
  unsigned int adc_at_fault[] = {
  0, 0, 0, 0, 0, 0, 0, 0
  };
*/



// fault ISR for reflex circuit
void reflex_fault()
{
  fault_flag = true;
}



void do_close()
{
  // low going pulse. Add delays around low if required (unlikely).
  digitalWrite(SHUTTER_CLOSE_PIN, HIGH);
  digitalWrite(SHUTTER_CLOSE_PIN, LOW);
  digitalWrite(SHUTTER_CLOSE_PIN, HIGH);

}

void do_open()
{
  // low going pulse. Add delays around low if required (unlikely).
  /*  if (!isTriggering()) */
  if (fault_flag == false)
  {
    digitalWrite(SHUTTER_OPEN_PIN, HIGH);
    digitalWrite(SHUTTER_OPEN_PIN, LOW);
    digitalWrite(SHUTTER_OPEN_PIN, HIGH);
  }
}


// the setup function runs once when you press reset or power the board
void setup() {
  Serial.begin(9600);
  Serial.println("initializing");
  pinMode(13, OUTPUT);
  digitalWrite(13, HIGH);

  //initialize pins
  pinMode(GET_SHUTTER_CLOSED_PIN, INPUT);
  pinMode(SENSOR_TRIGGERING_PIN, INPUT);

  digitalWrite(SHUTTER_OPEN_PIN, HIGH);
  digitalWrite(SHUTTER_CLOSE_PIN, HIGH);
  pinMode(SHUTTER_OPEN_PIN, OUTPUT);
  pinMode(SHUTTER_CLOSE_PIN, OUTPUT);

  // circuit always initializes with shutter is close position
  digitalWrite(SHUTTER_CLOSE_PIN, LOW);
  digitalWrite(SHUTTER_CLOSE_PIN, HIGH);

  // enable line for the first ADC
  digitalWrite(ENABLE_DEWAR_ADC_PIN, HIGH);
  pinMode(ENABLE_DEWAR_ADC_PIN, OUTPUT);

  // enable line for the second ADC
  digitalWrite(ENABLE_SHUTTER_ADC_PIN, HIGH);
  pinMode(ENABLE_SHUTTER_ADC_PIN, OUTPUT);

  // initialize falling edge interrupt on pin 3
  attachInterrupt(digitalPinToInterrupt(3), reflex_fault, FALLING);

  // for debugging
  /*
    for (int i = 0; i < 8; i++)
    {
    digitalWrite(ENABLE_SHUTTER_ADC_PIN, HIGH);
    delay(1000);
    digitalWrite(ENABLE_SHUTTER_ADC_PIN, LOW);
    delay(1000);
    }
  */

  // set CS to high
  digitalWrite(CS, HIGH);
  pinMode(CS, OUTPUT);

  // enable hardware SPI bus for communication with ADC boards via Diff Pair drivers
  SPI.begin();

  Serial.println("finished with initialization");
  digitalWrite(13, LOW);
}


// initialize sample time to current time to induce an immediate sample
unsigned long sample_time = millis();

// the loop function runs over and over again forever
// keep the main loop delay free

void loop() {
  // See if command is pending
  gatherSerial();

  if (millis() > sample_time)
  {
    sample_time += adc_interval; //sample at set interval period
    //do_ADC();
  }
}



void readDewarADC()
{
  int enable_pin = ENABLE_DEWAR_ADC_PIN;
  byte mask = B1111;

  digitalWrite(enable_pin, LOW);
  if (enable_delay > 0)
    delay(enable_delay);
  unsigned int val = 0;

  for (int i = 0; i < 8; i++)
  {
    // will mask i/2 and i/2+1 due to integral arithmetic
    if (mask & (1 << i / 2))
    {
      digitalWrite(CS, LOW);
      if (cs_delay > 0)
        delay(cs_delay);
      //SPI.setClockDivider(SPI_CLOCK_DIV128);
      SPI.setClockDivider(SPI_CLOCK_DIV64);

      SPI.transfer(B00000001);
      int y = SPI.transfer(B10000000 + (i << 4));
      int x = SPI.transfer(0x00);

      digitalWrite(CS, HIGH);

      y &= B00000011;
      val = (y << 8) + x;
    }
    else // if masked out, set the reading to 0, and the threshold to 255
    {
      if (i % 2 == 0)
      {
        val = 0;
      }
      else
      {
        val = 255; // max value is 1023. Using 255 as an easy to see "special" value indicating that the sensor is offline
      }
    }

    adc_data_dewar[i] = val;

#ifdef DEBUG
    Serial.println(val);
#endif
  }
  digitalWrite(enable_pin, HIGH);

#ifdef DEBUG
  Serial.println("------------------");
#endif

}

void readShutterADC()
{
  int enable_pin = ENABLE_SHUTTER_ADC_PIN;
  byte mask = B0001;

  digitalWrite(enable_pin, LOW);
  if (enable_delay > 0)
    delay(enable_delay);
  unsigned int val = 0;

  for (int i = 0; i < 8; i++)
  {
    // will mask i/2 and i/2+1 due to integral arithmetic
    if (mask & (1 << i / 2))
    {
      digitalWrite(CS, LOW);
      if (cs_delay > 0)
        delay(cs_delay);
      //SPI.setClockDivider(SPI_CLOCK_DIV128);

      SPI.transfer(B00000001);
      int y = SPI.transfer(B10000000 + (i << 4));
      int x = SPI.transfer(0x00);

      digitalWrite(CS, HIGH);

      y &= B00000011;
      val = (y << 8) + x;
    }
    else // if masked out, set the reading to 0, and the threshold to 255
    {
      if (i % 2 == 0)
      {
        val = 2048;
      }
      else
      {
        val = 2048; // max value is 1023. Using 255 as an easy to see "special" value indicating that the sensor is offline
      }
    }

    adc_data_shutter[i] = val;
  }
  digitalWrite(enable_pin, HIGH);

}

void doDewarADC()
{
  digitalWrite(ENABLE_DEWAR_ADC_PIN, HIGH); // pull enable on differential driver chips down
  readDewarADC();    // send I2C command to read ADCs
  faultOnDewarADC();                        // set fault true and close shutter
}

void doShutterADC()
{
  digitalWrite(ENABLE_DEWAR_ADC_PIN, HIGH); // pull enable on differential driver chips down
  readShutterADC();    // send I2C command to read ADCs
  //faultOnShutterADC();                        // set fault true and close shutter
}


// shuts the shutter if the ADC value is above the threshold value.
// this is a "backup" for the reflex circuit
// used a 0 to 4 loop, which I like better than the 0 to 8 loop in read_first_adc
// TODO: process needs to work on both raw adc data arrays

void faultOnDewarADC()
{
  // process first ADC
  for (int i = 0; i < 4; i++)
  {
    if (adc_data_dewar[2 * i] > adc_data_dewar[2 * i + 1])
    {
      fault_flag = true;
      //Serial.println("faulting!!");
      do_close();
    }
    /*
      for (int j = 0; j < 8; j++)
      {
      adc_at_fault[j] = adc_data_0[j];
      }
    */
  }

  // process second ADC goes here
}

// simple "command line" processer. Reads until it sees a linefeed, then attempts to process the whole line
// ignores carrage return
// upper cases data, to make parsing simpler
void gatherSerial()
{
  if (Serial.available() > 0)
    digitalWrite(13, HIGH);

  while (Serial.available() > 0)
  {
    int c = Serial.read();
    if (c == '\r') // ignore this character
    {
      //ignore
    }
    else if (c == '\n') // sentinal marking EOL
    {
      buf[bufPos] = '\0';
      bufPos = 0;
      processCommand();
    }
    else
    {
      buf[bufPos++] = toupper(c);
    }
  }
}

// exectute action based upon line received from serial line
void processCommand()
{
#ifdef DEBUG
  Serial.print("Processing: ");
  Serial.println(buf);
#endif

  if (strlen(buf) == 0)
  {
#ifdef DEBUG
    Serial.println("Did not see a command...   ");
#endif
  }

  else if (strncmp(buf, OPEN, strlen(buf)) == 0)
  {
#ifdef DEBUG
    Serial.println("# saw OPEN");
    Serial.println("openning shutter");
#endif
    do_open();

  }
  else if (strncmp(buf, "CLOSE", strlen(buf)) == 0)
  {
#ifdef DEBUG
    Serial.println("# saw CLOSE");
#endif
    do_close();
  }
  else if (strncmp(buf, "STATUS", strlen(buf)) == 0)
  {

    doDewarADC();
    doShutterADC();
    printStatus();

  }
  /*
    else if (strncmp(buf, "FAULT", strlen(buf)) == 0)
    {
    Serial.println("#Saw FAULT");
    Serial.println(fault_flag);
    if (fault_flag)
    {
      for (int i = 0; i < 8; i++)
      {
        Serial.print(adc_at_fault[i]);
        Serial.print(",");
      }
      Serial.println();
    }
    }
  */
  else if (strncmp(buf, "CLEAR", strlen(buf)) == 0)
  {
    Serial.println("#Saw CLEAR");
    Serial.println("#clearing fault");
    fault_flag = false;
  }
  else if (strncmp(buf, "DEWAR", strlen(buf)) == 0)
  {
    Serial.print("#Saw ");
    Serial.print(buf);
    Serial.print(" -> ");
    Serial.println("DEWAR");
    doDewarADC();
    printDewarStatus();

  }
  else if (strncmp(buf, "SHUTTER", strlen(buf)) == 0)
  {
    Serial.print("#Saw ");
    Serial.print(buf);
    Serial.print(" -> ");
    Serial.println("SHUTTER");
    doShutterADC();
    printShutterStatus();
  }
  else if (strncmp(buf, "HELP", strlen(buf)) == 0)
  {
    Serial.println("Commands available are: OPEN, CLOSE, STATUS, and HELP");
  }
  else if (strncmp(buf, "HELLO", strlen(buf)) == 0)
  {
    Serial.println("Hello!! How are you?");
  }
  else // bone plate
  {
    Serial.print("ERR: I do not understand: \"");
    Serial.print(buf);
    Serial.println("\". Type HELP to get a list of available commands");
  }
}

/*
  boolean isTriggering()
  {
  boolean x = digitalRead(SENSOR_TRIGGERING_PIN);
  if (x)
  {
    return false;
  }
  else
  {
    return true;
  }
  }
*/


void printDewarStatus()
{
  for (int i = 0; i < 8; i++)
  {
    if (i > 0)
      Serial.print(",");
    Serial.print(adc_data_dewar[i]);
  }
  Serial.println();
}

void printShutterStatus()
{
  for (int i = 0; i < 2; i++)
  {
    if (i > 0)
      Serial.print(",");
    Serial.print(adc_data_shutter[i]);
  }
  Serial.println();
}

void printStatus()
{
  boolean is_closed = digitalRead(GET_SHUTTER_CLOSED_PIN);
  Serial.print(is_closed);
  Serial.print(",");
  Serial.print(fault_flag);
  Serial.print(",");

  for (int i = 0; i < 8; i++)
  {
    if (i > 0)
      Serial.print(",");
    Serial.print(adc_data_dewar[i]);
  }

  Serial.print(",");

  for (int i = 0; i < 2; i++)
  {
    if (i > 0)
      Serial.print(",");
    Serial.print(adc_data_shutter[i]);
  }

  Serial.println();
}

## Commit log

2017-06-02 Sensor board that we are manufacturing via OSHPARK order number ucyGHMt4
    [Sensor Board v2.brd]
2017-06-02 Sensor board that was sent for manufacture with OSHPARK order number ucyGHMt4
    [Sensor Board v2.sch]
2017-06-02 ADC Boards that were sent for manufacture via OSHPARK order number Ufq3rBYH
    [ADC board 2.brd, ADC board 2.sch]
2017-09-01 Added .gitignore file and initial version of Shutter schematic
    [Shutter.sch]
2017-09-14 Added two images which show/illusrate the wiring of the boards. Important for software developement and debugging.
2017-11-02 Updates to schematic. Definitely not done yet!
    [Shutter.sch]
2017-11-02 Software to run on ATMega328P programmed via Arduino IDE
2017-11-04 Update schematic to reflect current circuit. Change names of some nets to match sofware variables.
    [Shutter.sch]
2017-11-04 Change some variables/constants to better match function on board.
2017-11-04 Adding board file. This file has not been worked on.
    [Sensor Board.brd]
2017-11-04 Added board corresponding to Shutter.sch. This file has not been worked on yet.
    [Shutter.brd]
2017-11-04 Remove Sensor Board.brd from repository. This was an old design which did NOT work.
    [Sensor Board.brd]
2017-11-04 Added screw terminals for toggles.
    [Shutter.brd, Shutter.sch]
2017-11-08 Add PDF version of ADC board schematic.
2017-11-09 Added Shutter circuit schematic.
2017-11-09 Digikey Bills of Material for the ADC Circuit and the Diode Circuit.
    [ADC board 2 BOM.csv, Sensor Board v2 BOM.csv]
2017-11-17 Changed feedback resistor value to match currently used on board.
    [Sensor Board v2 BOM.csv]
2017-11-17 Added descriptions to BOM
    [Sensor Board v2 BOM.csv]
2017-11-17 Added OD buffer schematic to complete Shutter Circuit Schematic.

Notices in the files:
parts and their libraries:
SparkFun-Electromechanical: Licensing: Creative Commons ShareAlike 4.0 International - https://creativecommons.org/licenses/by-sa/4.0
